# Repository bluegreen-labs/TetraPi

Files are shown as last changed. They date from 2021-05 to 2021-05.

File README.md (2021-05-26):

# TetraPi

Schematics for a 3D printable housing and build instructions for a multispectral Raspberry pi camera. The camera relies on off the shelve components and provides a cost effective and easily maintained alternative to commercial cameras. The camera is built around a Raspberry pi type A or A+, a four camera multiplexer, four 5 or 8 MP Raspberry pi cameras and standard 25mm diameter filters (a common format for benchtop optics).

The camera has three main parts, the main housing, a top plate fitting the four cameras and optical filters and cover plate which holds the filters in place. For coloured glass filters a padding ring is provided so the filter is held in place. The top plate and cover plate are screwed into place using M3 screws (using brass threated inserts). The main housing has flanges to provide easy mounting (3 mm mounting holes). A backing plate with a 1/20" camera screw is provided for mounting the camera on a standard tripod.

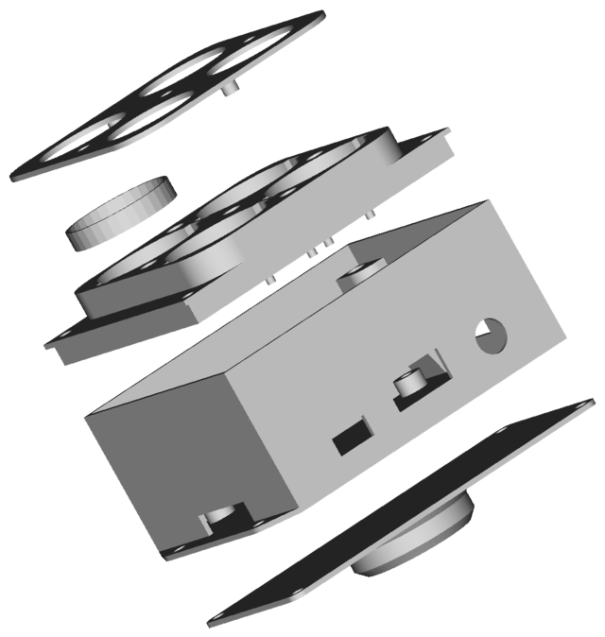
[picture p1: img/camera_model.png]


## Camera build

### Main housing

Mount the Raspberry pi A(+) in the housing on the printed stand-offs, using M2.5 screws and bolts. Attach the ribbon cables which are provided with Raspberry pi cameras to the multiplexer board. When mounting the multiplexer board onto Raspberry pi fold the ribbon cables under the board so they all exit at one side of the raspberry pi, inbetween both boards.

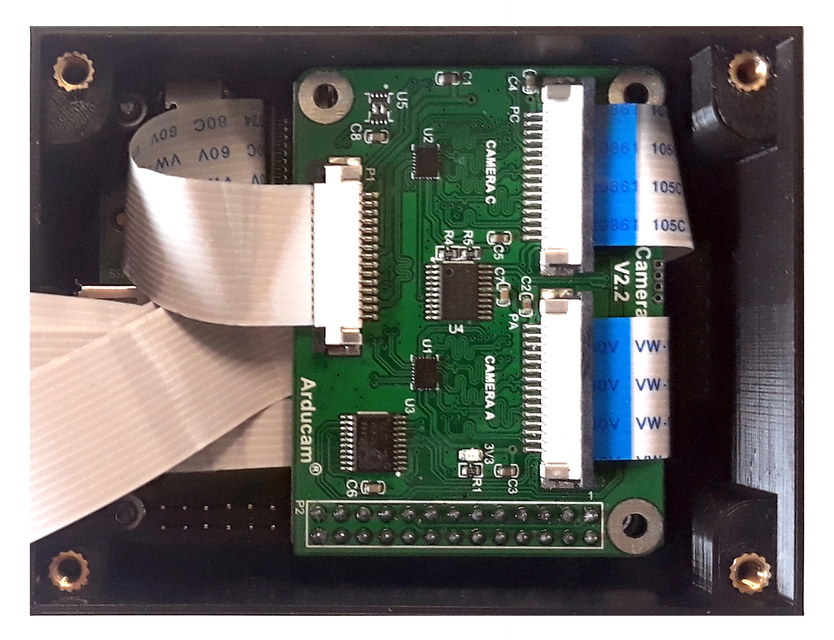
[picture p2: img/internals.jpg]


### Top plate

Recent batches of the Raspberry pi (NOIR) cameras come mounted with the image sensor on flexible foam double sided tape. This original setup doesn't allow for easy and predicable alignment of the cameras. To fix this issue, remove the sensor and remount it using thin double sided tape. In some cameras this setup is the default already, if you are lucky you can skip this step.

|Original | Modified |
|:----:|:----:|
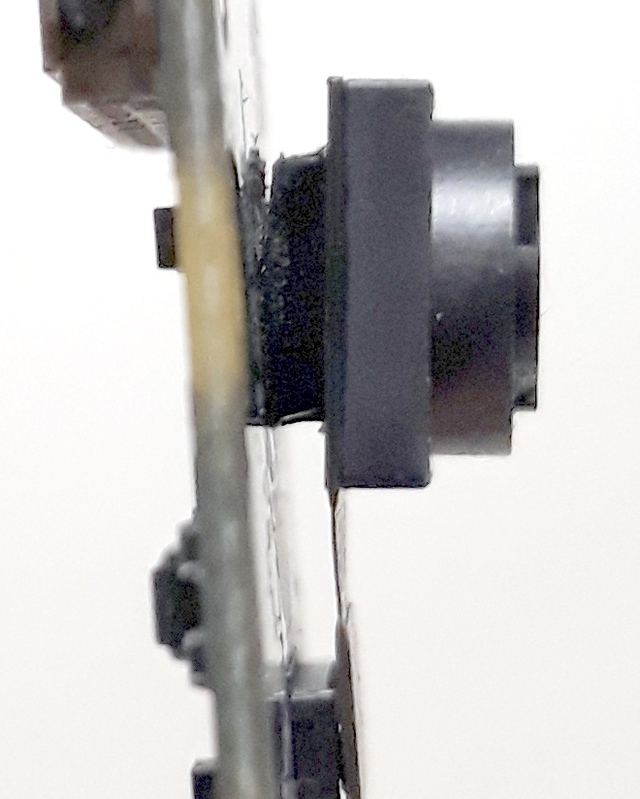
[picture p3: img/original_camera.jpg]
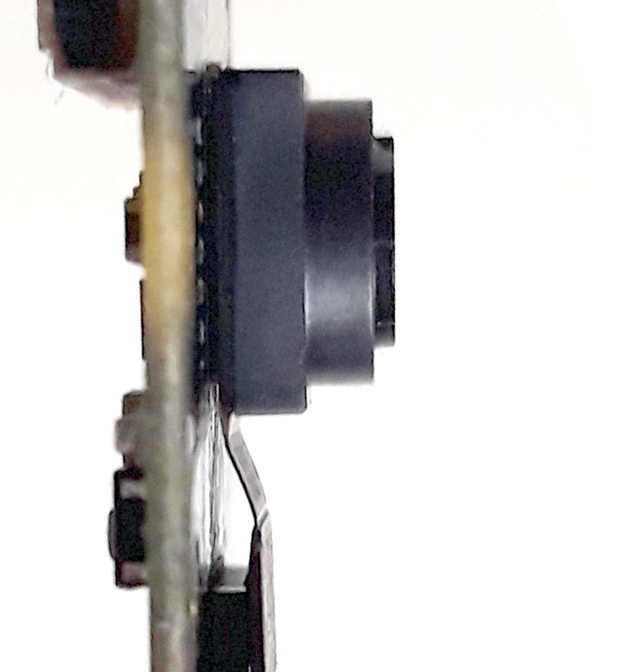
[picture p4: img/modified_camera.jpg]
|  |  |

Mount the cameras using double sided tape, fitting the mounting holes over the printed poles to provide a friction fit. If you are testing a system the tiny poles should provided enough support to keep the cameras in place. For long term applications do use tape as extra support. Be careful while manipulating the cameras as the tiny poles are fragile and can snap if you exert too much pressure.

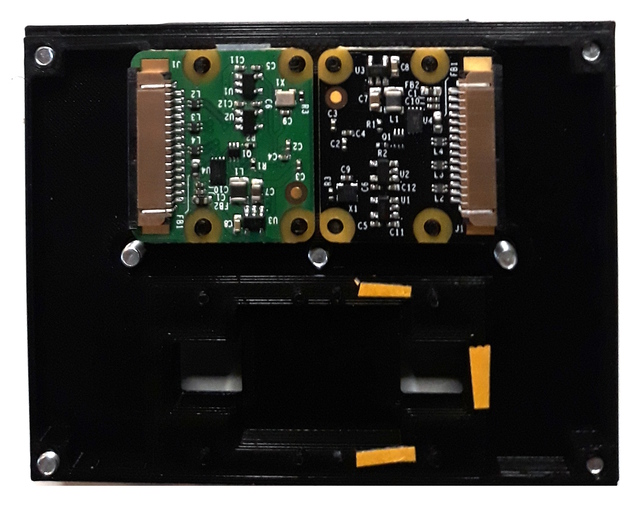
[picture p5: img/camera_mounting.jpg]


Carefully connect the ribbon cables to all cameras, routing them appropriately. Push down on the cables gently while closing the top cover, making sure you don't cover the screw holes.

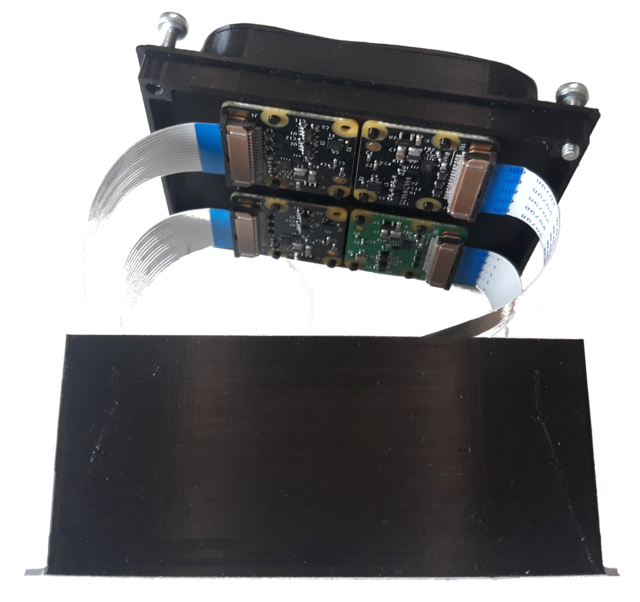
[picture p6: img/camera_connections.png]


### Filter plate

Finally, install your filters in the filter holes. When using glass filters provide additional padding with a filter ring to prevent the filter from rattling and being damaged (especially on moving platforms). Cover the the filter assembly with the filter plate and screw down firmly.

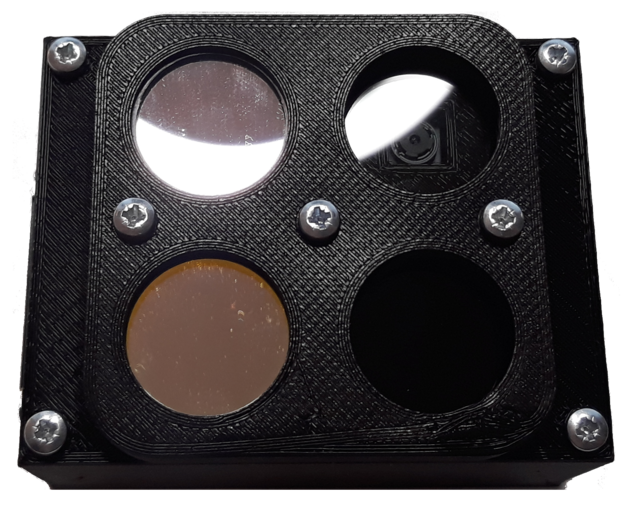
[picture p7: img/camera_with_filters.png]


## Specifications

| | |
|--|--|
| **filters**| 2 - 4 (max) |
| **filter type** | 25mm benchtop filters (e.g. Thorlabs) |
| **weight**| ~150gr (as shown) |
| **storage** | limited by internal SD card, cloud services (wifi) or external USB drive |

## Bill of Materials (as shown)

The cost of the system varies significantly with the quality of the filters used, or the cameras mounted. In the described setup focussing on vegetation indices (EVI and PRI), the laser line filter makes up 25% of the assembly. Using more or less expensive filters will change the price dramatically. The overall price without any filters (or special cameras) comes to 230 EURO (not including 3D printing costs). Beware that hardware modifications for the Rasperry pi cameras exist, in particular there is a monochrome UV capable modification sold by [MaxMax](https://maxmax.com/maincamerapage/monochrome-cameras/raspeberry-pi-cameras/raspberry-pi-mono) (~500 EURO), extending the setup into the UV domain (for direct or fluorescence measurements, or [forensic measurements](https://www.mdpi.com/1424-8220/16/10/1649)). The header allows for the extension of the setup into the thermal infrared using a FLIR lepton camera unit. Due to current chip shortages I've not included this in the current version. The FLIR camera is expensive (~300 EURO) but would increase the spectral domain of the build considerably. For custom builds please contact [BlueGreen Labs](https://bluegreenlabs.org).

| Item | price (EURO)|
|--|--|
| **530nm laser line filter**| 130 |
| **570nm bandpass filter**| 80 |
| **NIR filter**| 30 |
| **VIS filter**| 30 |
| **Raspberry pi A(+)** | 35 |
| **multiplexer board**| 50 |
| **Raspberry pi cameras (4x)** | 140 |
| **3D printing** | free or cheap at a makerspace / institutional workshop |
| **threated inserts (M3 / 1/20")** | 5 |
| **TOTAL**| ~ 500 |

## Notes

The Raspberry pi (3) A+ with the faster processor and onboard wifi should probably be avoided for continuous applications. The system is tightly packed and therefore runs hot and overall requires more power than desired (especially for offline use). Using the a Raspberry pi (2) A board avoids these thermal and power issues, while sacrificing internal wifi. Wifi can be added using a USB stick. Future versions might include more venting holes and a smaller (lighter) build around a Raspberry pi Zero. For development purposes I do recommend the Raspberry pi (3) A+ as it makes interacting with the camera faster.

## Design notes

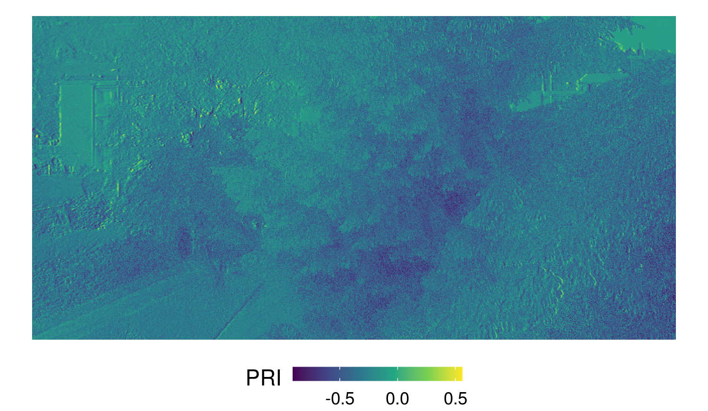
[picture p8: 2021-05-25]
img/PRI.png

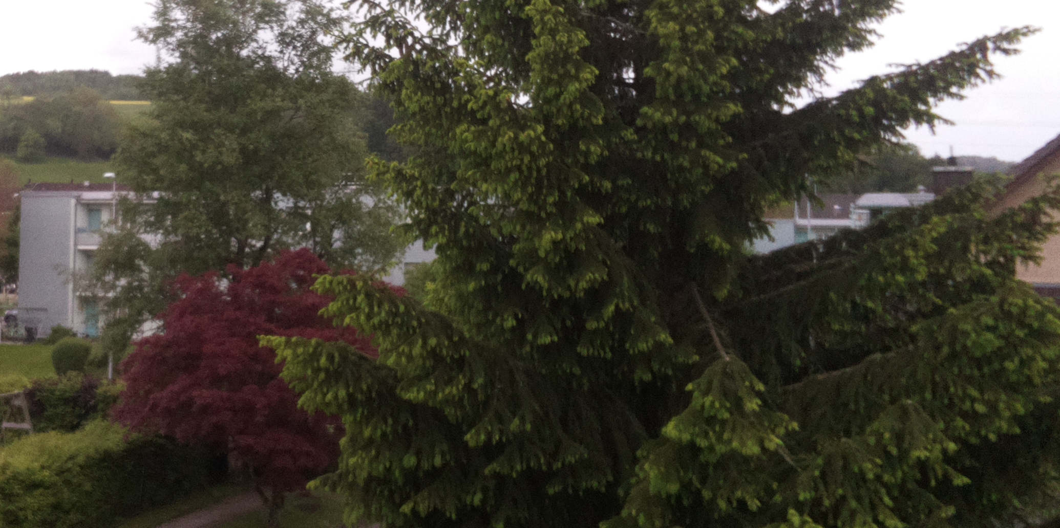
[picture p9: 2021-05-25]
img/rgb.jpg

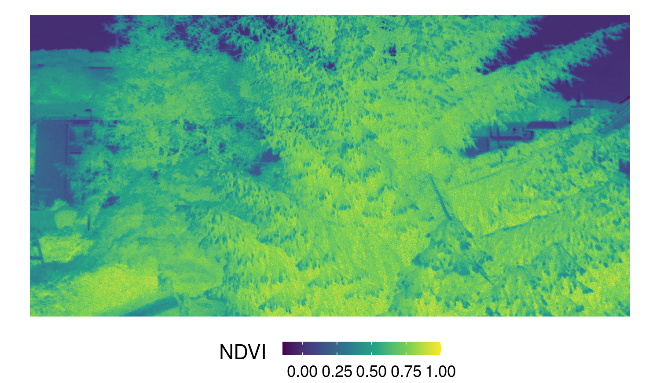
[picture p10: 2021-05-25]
img/NDVI.png

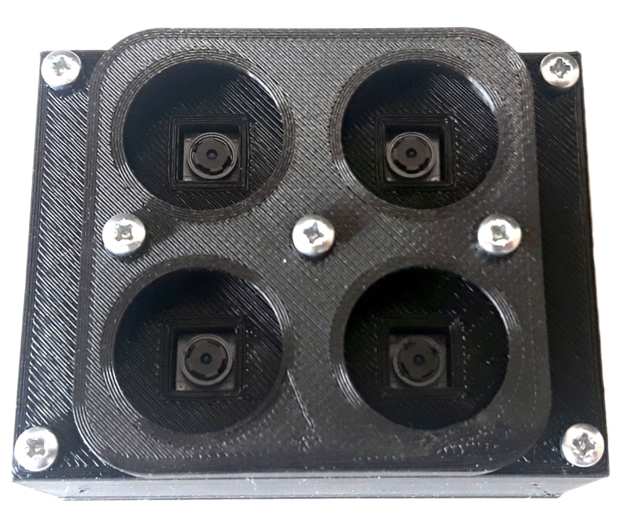
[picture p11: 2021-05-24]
img/camera_no_filters.png

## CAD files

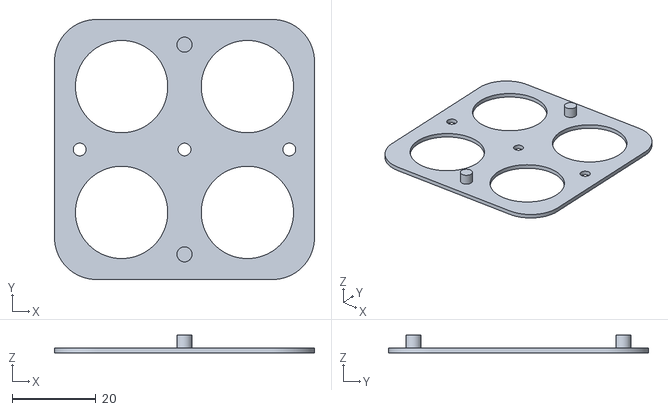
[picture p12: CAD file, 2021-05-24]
stl/filter_plate.stl
62.0 x 62.0 x 4.20

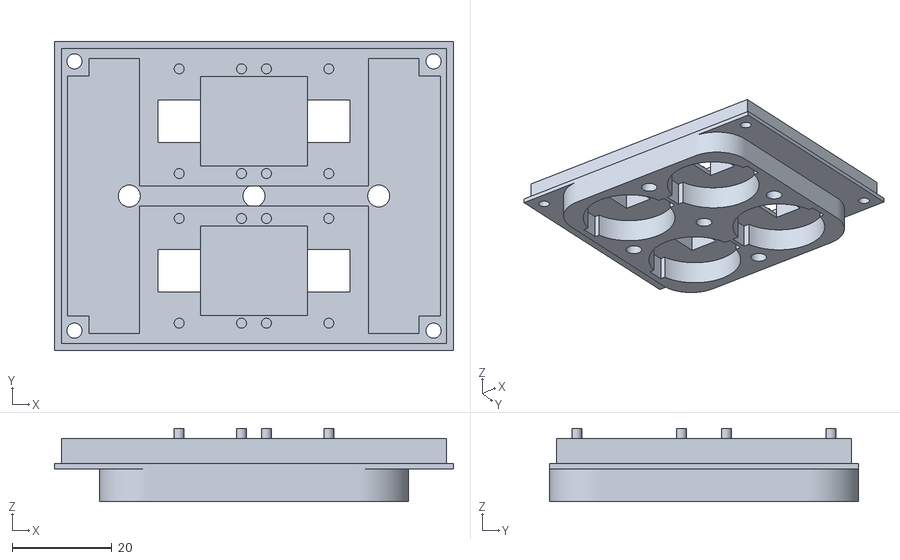
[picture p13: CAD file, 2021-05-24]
stl/housing_top.stl
80.0 x 62.0 x 14.7

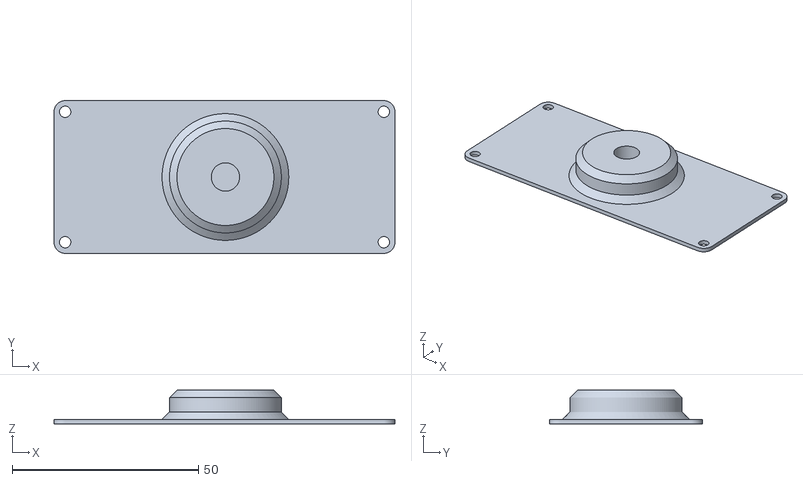
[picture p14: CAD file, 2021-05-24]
stl/tripod_mount_plate.stl
91.5 x 41.0 x 9.00

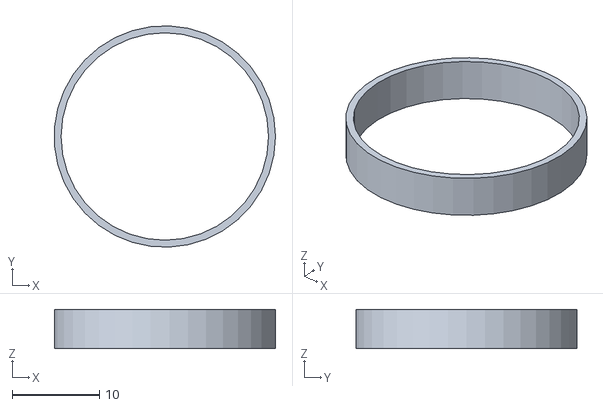
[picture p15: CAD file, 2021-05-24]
stl/filter_ring.stl
25.4 x 25.4 x 4.50

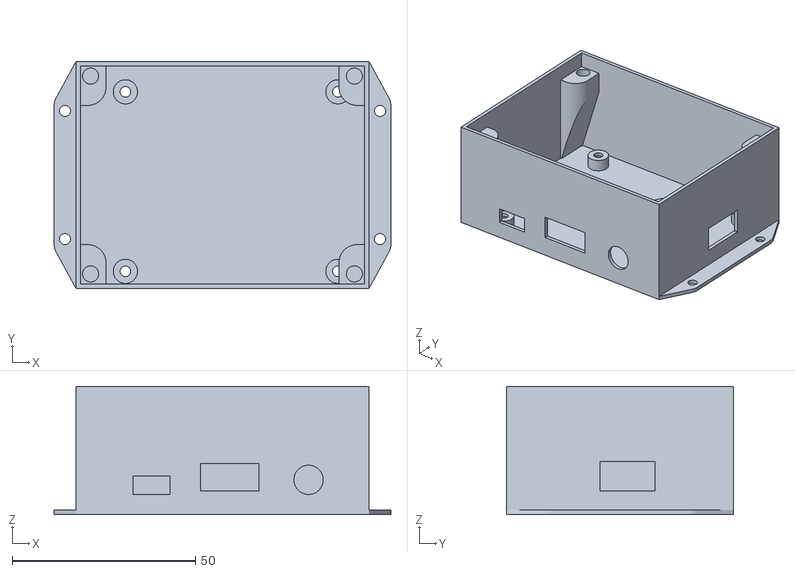
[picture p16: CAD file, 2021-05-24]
stl/housing.stl
92.0 x 62.0 x 35.0
